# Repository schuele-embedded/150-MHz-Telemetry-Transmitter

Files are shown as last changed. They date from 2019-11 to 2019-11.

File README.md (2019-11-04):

# 150-MHz-Telemetry-Transmitter
Ultra Low Power VHF-Transmitter for Wildlife Radio Tagging

This Transmitter is an adaption of http://http://people.ece.cornell.edu/land/PROJECTS/TRANSMIT/.<br>
It has some minor changes and uses only discrete components as winding all coils etc. manually needs a lot of experienece, luck and effort to get the circuit running well and robust, which I hardly had to experience...
I got two versions running stable, one manufactured in THT and one in SMD.

This circuit allows to build a low-cost, tiny, light weight and very low power VHF-pulse-transmitter from scratch.
It's purpose is to be used in scientific tracking applications for wildlife and livestock.
This is the easiest but most effective transmitter circuit which is known to me.

This circuit is operating on 150 MHz and as all radio transmitters also emitting electromagnetic waves at harmonic frequencies, so be sure that you now your local rules for the emitted frequency spectrum! This report is only a theoretical abstract so there is no legal  warranty.

This circuit is based on developments in the early 70s on radio telemetry for wildlife and still base for many transmitters nowadays.
Check also R. Kenwards book "A manual for wildlife radio tagging" if you're interested in further information and advanced knowledge in radio tagging.

The circuit is in principle a very simple single-stage oscillator based on the third harmonic of a 50MHz crystal (you can also use a different frequency crystal). Its emitting short pulses of a continuous wave signal.
The pulse width and pulsing frequency is determined by a simple RC-network. 
This transmitter can also be used for simple data modulation using ASK (Amplitude Shift Keying) with On-Off-Keying (OOK) by removing the components Rp and Rc and turning on/off the oscillator by applying/removing voltage (with levels Uin/GND) directly to resistor R1 (Node "EN").

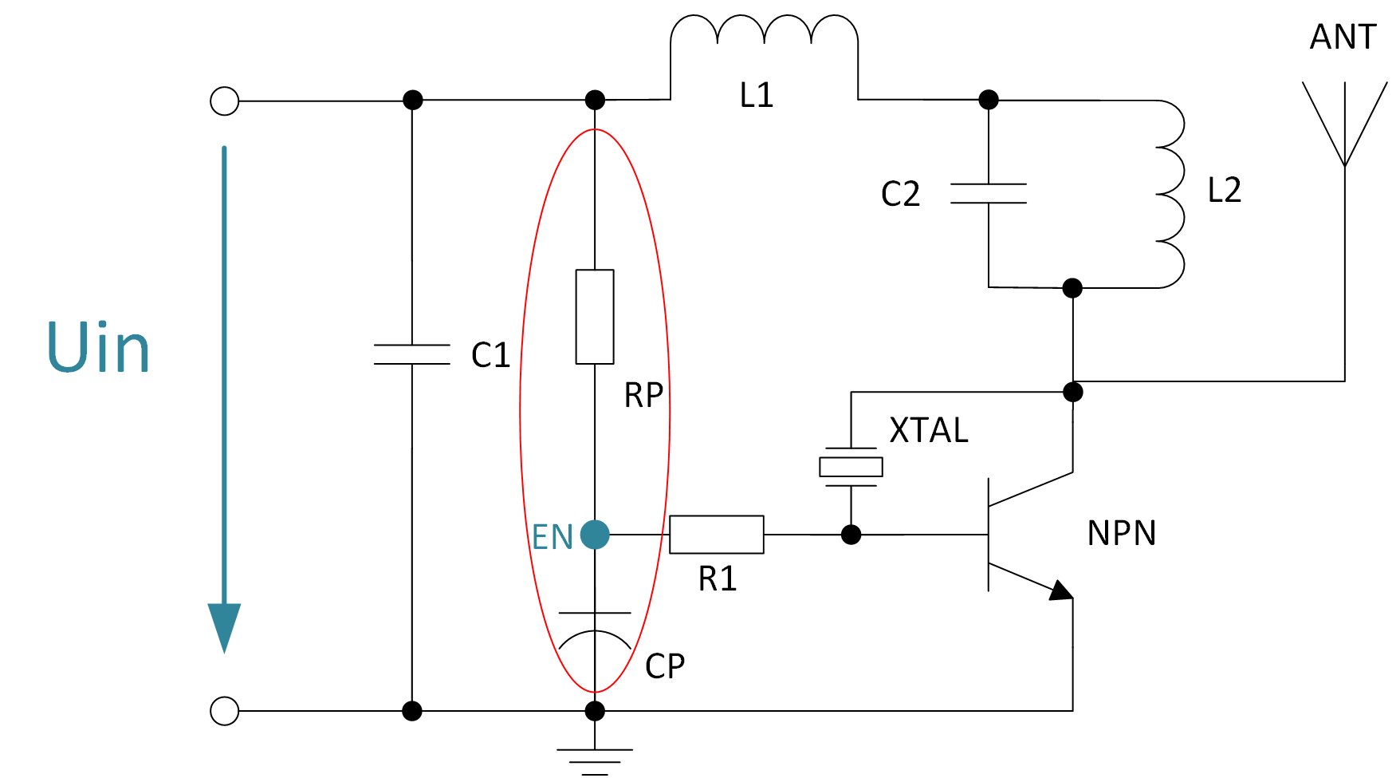
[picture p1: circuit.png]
Circuit of Low-Power VHF-Transmitter


Best results were found with the following values:

C1 = 100 nF<br>
L1 = 100 nH (In THT wind copper coil: 4x0.4mm, diameter 3mm)<br>
R1 = 390 kOhm<br>
C2 = 15 pF<br>
L2 = 1 µH (In THT wind copper coil: 12x0.4mm, diameter 3mm)<br>
NPN = MMBT3904 (In THT: 2N3904)<br>
XTAL = 50 MHz<br>
3rd harmonic determines transmitter frequency<br>

Rp = 0-1 MOhm<br>
Cp = 0-5 µF<br>
Combination of Rp and Cp determine the pulse width and Pulsing frequency.

This circuit can be build on a small pcb (see also eagle schematic and layout in ".../eagle/") or directly solder the THT components to each other as a "flying assembly".
As antenna you can use just a piece of copper wire with length lambda/4 which is for 150MHz: 2m/4 = 50 cm

The PCB SMD version got an additional matching capacitor Cm with value 2.2pF which was added in series to the antenna.

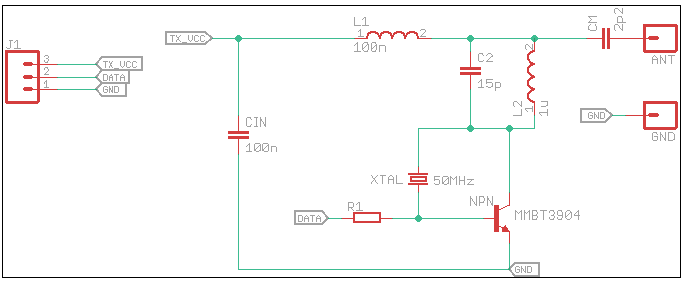
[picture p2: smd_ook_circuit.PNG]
Circuit used for ASK/OOK

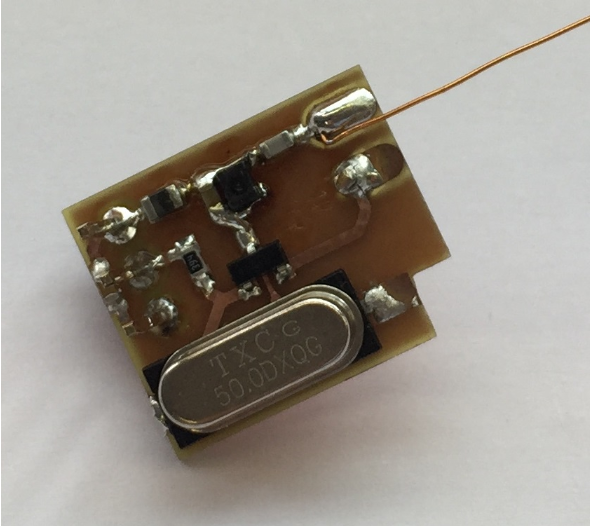
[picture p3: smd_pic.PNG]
Assembled Transmitter SMD version


Some characterization results:

The supply voltage can be as low as 0.7V and the circuit consumes only 1.5 mA @ 2.5V.
A simple, small, light coin cell with 1.5V for example can be used as power supply.

Maximum datarate is 250 baud with ASK/OOK modulation.

This graph shows the relative emitted power at harmonic frequencies and the narrow signal at 150 MHz.
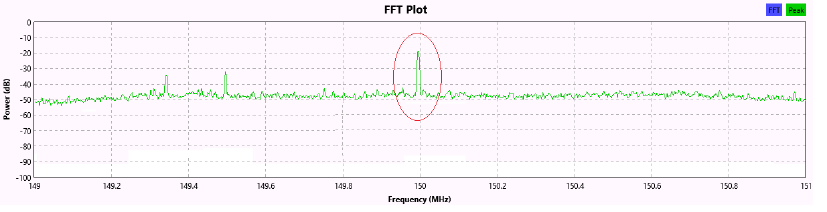
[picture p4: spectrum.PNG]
Frequency Spectrum

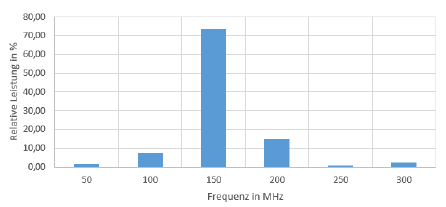
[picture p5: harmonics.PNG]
Radiated Power at Harmonics


As receiver a very low cost china handheld device Baofeng UV-5R (30€) was used and a Telonics RA-14 H-antenna which is matched to 150 MHz. 

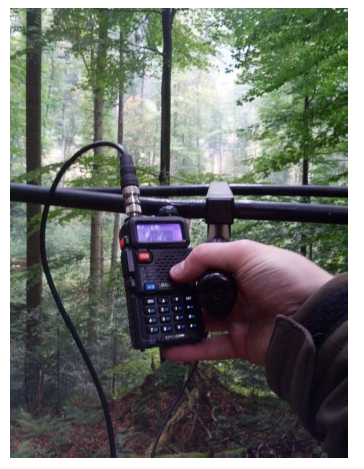
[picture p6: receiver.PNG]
Receiver UV-5R and RA-14


With this setup a maximum distance through forest was found at even 350m.

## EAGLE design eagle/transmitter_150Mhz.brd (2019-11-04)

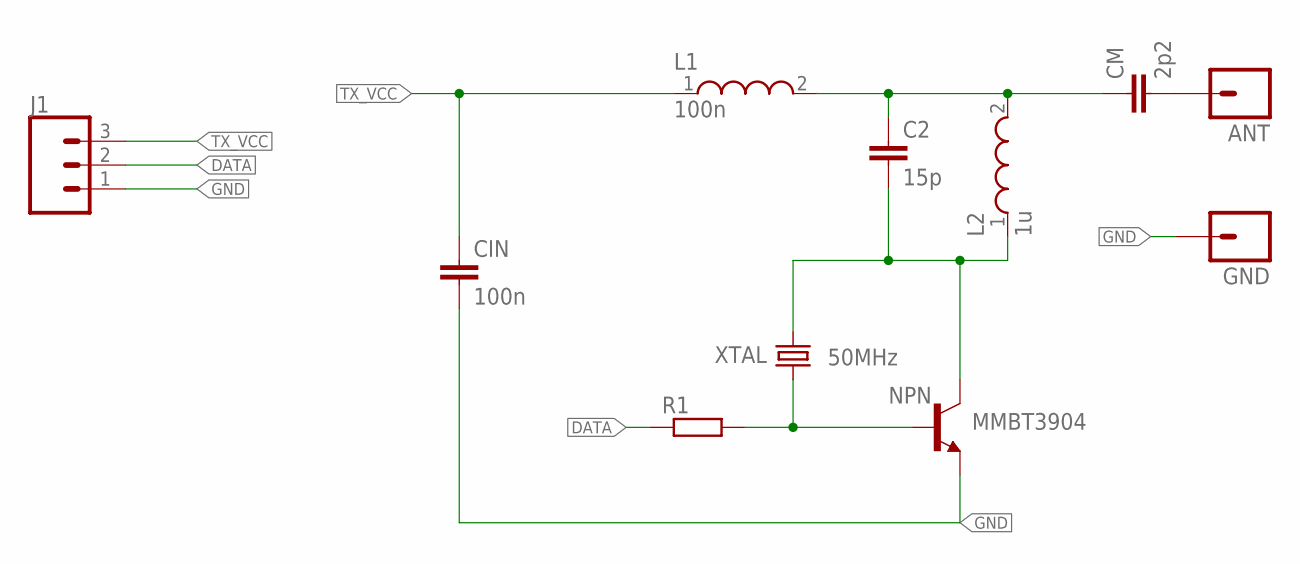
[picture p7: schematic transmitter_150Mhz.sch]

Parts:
ANT: M01OFFSET; 1X01_OFFSET
C2: 15p; C0603
CIN: 100n; C0603
CM: 2p2; C0603
GND: M01OFFSET; 1X01_OFFSET
J1: CONN_03; 1X03
L1: 100n; WE-PMI_0805
L2: 1u; WE-PMI_0806
NPN: MMBT3904; SOT23-BEC
R1: R-EU_R0603; R0603
XTAL: 50MHz; SM49

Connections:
ANT: C2.1, CM.1, L1.2, L2.2
DATA: J1.2, R1.1
GND: CIN.2, GND.1, J1.1, NPN.E
unnamed: ANT.1, CM.2
unnamed: NPN.B, R1.2, XTAL.1
unnamed: C2.2, L2.1, NPN.C, XTAL.2
TX_VCC: CIN.1, J1.3, L1.1

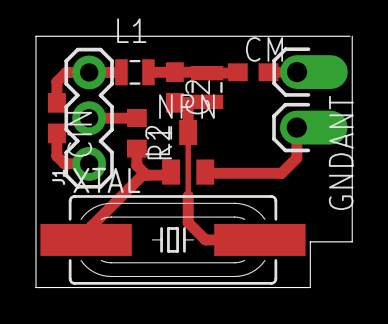
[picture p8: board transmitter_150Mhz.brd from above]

Board: 2 copper layers, 17.6 x 14.0 mm, 11 parts (0 on the bottom side), 7 nets.

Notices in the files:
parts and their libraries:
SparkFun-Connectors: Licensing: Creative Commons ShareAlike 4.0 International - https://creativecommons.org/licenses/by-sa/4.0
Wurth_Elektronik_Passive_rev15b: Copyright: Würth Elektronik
